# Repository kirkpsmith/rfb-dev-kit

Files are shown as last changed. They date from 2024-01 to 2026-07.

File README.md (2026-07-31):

# RFB-dev-kit



[Certified](https://certification.oshwa.org/fr000028.html) by OSHWA

--------------------------------------------------------------------------------
## About

This kit is for testing flow battery components and electrolytes at a benchtop scale (2 cm²) with an affordable, reproducible setup.

Developed by the [Flow Battery Research Collective](https://fbrc.dev).

Assembled cell

View of electronics in jig

## Documentation

Documentation to build the kit, which includes the BOM, is available [here (latest version, with file previews)](https://fbrc.codeberg.page/rfb-dev-kit/), or locally in the repo [here (current version, without file previews)](docs/_site/index.html).

## Design Choices

- Maximize off-the-shelf component and material availability.
- Impervious graphite or polymer-graphite composite materials are hard to source. Instead we use graphite foil, which is affordable, easily sourceable and works well enough to perform cycling experiments at this scale.
- No flow fields. We use flow-through graphite felt porous electrodes, and the design is parametric to handle different thicknesses
- No milling of graphite or plastic.

## Repository Structure

- `CAD` directory: FreeCAD and KiCAD design files
    - `FreeCAD` directory: FreeCAD files
    - `KiCAD` directory: KiCAD project files
    - `exports` directory: files for manufacturing components and rendering documentation
    - `imports` directory: files imported by FreeCAD for creating assembly
- `docs` directory: documentation written with [GitBuilding](https://gitbuilding.io/)
- `firmware` directory: code for pump speed controllers based on Arduino Uno R3

## Contributing

Please see the [contributing guide](https://fbrc.dev/contributing.html) on our website!

## Community

Discussion about the project happens on the [FBRC forum](https://fbrc.nodebb.com/)!

## References/Inspiration/Collaborators/Conspirators (in no particular order)
- [FAIR Battery project](https://github.com/SanliFaez/FAIR-Battery) (collaborators)
- White, R. E. Electrochemical Cell Design; Springer US: Boston, MA, 1984.
- O’Connor, H.; Bailey, J. J.; Istrate, O. M.; Klusener, P. A. A.; Watson, R.; Glover, S.; Iacoviello, F.; Brett, D. J. L.; Shearing, P. R.; Nockemann, P. An Open-Source Platform for 3D-Printed Redox Flow Battery Test Cells. Sustainable Energy Fuels 2022, 6 (6), 1529–1540. https://doi.org/10.1039/D1SE01851E.
- Arenas, L. F.; Walsh, F. C.; León, C. P. de. 3D-Printing of Redox Flow Batteries for Energy Storage: A Rapid Prototype Laboratory Cell. ECS J. Solid State Sci. Technol. 2015, 4 (4), P3080. https://doi.org/10.1149/2.0141504jss.
- https://codeberg.org/LibreWater/Acraea-Prototype
- https://github.com/opulo-inc/lumenpnp/tree/main
- https://openflexure.org/

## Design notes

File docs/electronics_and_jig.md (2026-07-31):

---
Details:
    Time: Tens of minutes
    Skills:
      - Soldering
      - Flashing firmware to an Arduino 

---
<!-- There should be only one Header per page. You do not need to use all the keys -->
# Preparing the jig with pumps and power electronics

{{BOM}}

## System overview

A [computer]{cat:tool, qty:1, Note:Must be able to flash firmware to microcontroller and connect over USB serial to microcontroller and potentiostat} communicates with both a charging/discharging device (typically a [potentiostat](pstat.md){cat:tool, qty:1, note: preferably the MYSTAT}) as well as an [Arduino UNO R3]{qty:1, Note:or equivalent microcontroller that can output two independent 5V PWM signals and connect to the computer over USB serial}. These documents assume the use of a MYSTAT potentiostat and it's [modified control software](https://codeberg.org/FBRC/mystat/).

The Arduino is connected to two peristaltic pumps which have internal stepper motor drivers, and are powered by a [24 V DC power source]{cat: part, qty: 1}. To know the flowrate (in mL/min) of the peristaltic pumps, a separate measurement is required (like dispensing water into a graduated cylinder).

We use the open-source MYSTAT (with our own modifications to the control software), but any equivalent potentiostat or battery cycler will do. Our pump control system is based on the MYSTAT software, though, and can be used without the MYSTAT present.

With this hardware configuration, the MYSTAT software then allows for entire control of this electrochemical system: the applied currents and voltages as well as the speeds of the electrolyte pumps. 

## Flash firmware to microcontroller {pagestep}

Using the Arduino IDE with the elapsedMillis library installed, upload the following code to the Arduino. The location of the code in the repository is [here](https://codeberg.org/FBRC/RFB-dev-kit/src/branch/main/firmware/ArduinoUnoR3_MotorControl.ino)

## Solder the wiring harness

Using a [soldering iron]{cat: tool, qty: 1}, take the [peristaltic pumps with correct tubing](fromstep){qty: 2}, [DC power jack]{cat: part, qty: 1} and solder them to the Arduino according to the following schematic:


>! **Caution** 
>!
>! Be sure to connect the Arduino ground to the power supply ground of the pumps so that the PWM and tachometer signals work properly

## Assemble the pump controller case

Taking the soldered Arduino, pumps, and DC power jack, assemble them into the [pump controller case parts](fromstep){qty: 1} as shown:



The pump wiring is fed through the long narrow slots in the pump controller case base so that it can be assembled into the case post-soldering.

## Add pumps and controller case to jig {pagestep}

Insert the pumps into their holders in jig while aligning the pump controller case mounting holes with their matching holes on the jig. Fasten with eight [M3x35mm socket cap bolts and nuts]{qty: 8,cat: part}.



>i **Note** 
>i
>i The reset button is placed with the large end *inside* the case

##Connect microcontroller to PC and test pumps{pagestep}

We are using the MYSTAT potentiostat and have modified the software to be able to control the pump speeds. If you have a different potentiostat, you can still use the MYSTAT software to control your pumps without having a MYSTAT connected.

Plug in the 24V power supply cable to the jack on the case.. Connect the Arduino to the PC with a [USB A-to-B cable]{qty: 1,cat: part}.

Run the MYSTAT [modified control software](https://codeberg.org/FBRC/mystat/releases).

Connect to the Arduino through the MYSTAT GUI. Briefly test each pump to make sure it spins (it can spin for a couple seconds dry without issues).



## Add tubing and connectors to top pump connections {pagestep}

Add two pieces of [4 cm cut tubing](fromstep){qty: 2} to the upper barbed fittings of each pump. Add a [F-31 Luer Lock Adapter][F-31 Luer Lock Adapters]{cat: part, qty: 2} to the other end of each piece of tubing.

>i **Note** 
>i
>i The tubing here is shown bent according to it's final shape after cell assembly, this will happen naturally when the cell is installed.



## Add reservoirs to jig {pagestep}

Insert the [combined reservoir with tubing](fromstep){qty: 1} into the jig as shown, connecting the shorter tubing on the inner barbs of the reservoirs to the bottom connection of the pump. The reservoirs should "click" into place into the holding mechanism on the jig.
The flexible tubing will eventually take on a shape similar to what is shown when the cell is installed.



[assembled jig]{output, qty: 1}

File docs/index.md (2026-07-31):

# Building a benchtop flow battery test cell

>i **Note** 
>i
>i This kit is intended for educational and R&D use only, not for actual energy storage applications. That will happen later, check out our [roadmap](https://fbrc.dev/about.html#roadmap) to see when.
>i
>i Project homepage is at https://fbrc.dev, source code for this documentation is [here](https://codeberg.org/FBRC/RFB-dev-kit).





This bill of materials can be found [here]{BOM}.

If you're starting from scratch, you need to [fabricate](fabrication.md) and source everything needed for using this flow battery test cell.

If you already have all the required components and materials, you can directly [prepare the electronics and jig](electronics_and_jig.md), [assemble the cell](cell_assembly.md), [install the cell into the jig](final_jig_assembly.md], prepare the [electrolyte](electrolyte.md), [leak test](leak_test.md) and then begin [testing](testing.md). After an experiment, you should [clean up](cleanup.md) your setup and [analyze](analysis.md) the data you obtained.

1. [.](fabrication.md){step}

2.  [.](electronics_and_jig.md){step}

3. [.](cell_assembly.md){step}

4. [.](final_jig_assembly.md){step}

5. [.](leak_test.md){step}

6. [.](electrolyte.md){step}

7. [.](testing.md){step}

8. [.](cleanup.md){step}

9. [.](analysis.md){step}

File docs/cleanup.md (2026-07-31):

---
Details:
    Time: Tens of minutes
    Skills:
      - General chemistry laboratory skills 
---
<!-- There should be only one Header per page. You do not need to use all the keys -->
# Stopping and disassembling the cell

Once your experiment has concluded, save your data files, power down and disconnect the potentiostat.

Stop the pumps and drain the electrolyte from the reservoirs into a waste container. Add water and run the pumps for several seconds to rinse the cell and tubing. Repeat until the drained solution is clear.

Handle chemical waste according to local regulations.

Disconnect the cell from the jig in four locations, leaving the tubing attached to all four barbs/ports of the two flow frames:

- at each pump, going from the pump to the flow frame (x2)
- at the double-ended barbed fittings between the flow frame and the reservoir inlet (x2)



Take apart the cell, noting that you can leave the tubing attached to the flow frames.

Make any observations you might have of the separator (note which way it was facing when you do so), positive and negative electrodes, *etc.*

Clean and store the reusable cell components.

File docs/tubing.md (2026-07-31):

---
PartData:
    Specs:
        Brand: Masterflex
        Type: Chem-Durance Bio Tubing
        Inner Diameter: 3.2 mm
        Outer Diameter: 6.4 mm
    Suppliers:
        Drifton (EU):
            PartNo: 06442-16
            Link: 'https://www.drifton.eu/shop/18-standard-pump-tubing/2535-chem-durance-bio-tubing-15-m/'
        Avantor (US):
            PartNo: 06442-16
            Link: 'https://www.avantorsciences.com/us/en/product/NA5143626/masterflex-ls-precision-pump-tubing-chem-durance-bio-avantor'
---

# Tubing

This tubing is made from a BPT-like exterior tubing with a PTFE-like liner which is good for flow battery chemical compatibility. It used to be called "Tygon Chemical" tubing and still is in some places.

>!! **Warning** 
>!!
>!! PTFE-lined tubing in the pump head is essential for electrolytes which contain iodide, as charged iodide species can destroy common pump head tubing materials like silicone and BPT



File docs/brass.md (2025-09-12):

---
PartData:
    Specs:
        Thickness: 1.0 mm
    Suppliers:
        Amazon:
           PartNo: Use this link
           Link: 'https://www.amazon.com/dp/B0BRCXM73P'

---

## Brass current collectors



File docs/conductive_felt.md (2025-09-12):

---
PartData:
    Specs:
        Material: Conductive Graphite Felt
        Thickness:  3.2 mm or 1/8 inch
    Suppliers:
        Fisher Scientific:
            PartNo: AA43199RY 
            Link: 'https://www.fishersci.com/shop/products/carbon-felt-3-18mm-0-125in-thick-99-0-thermo-scientific/AA43199RY#?keyword=043199'
        AliExpress:
            PartNo: Link
            Link: 'https://www.aliexpress.com/item/1005008240523112.html'

---

# Conductive Graphite (Carbon) Felt
The Fisher Scientifics carbon felt is commonly used in academic studies. There are other more affordable suppliers on AliExpress and specialty carbon product suppliers in various regions worldwide. The felt needs to be conductive, this technically means it has to have been "graphitized" and thermally treated at a sufficiently high temperature, though sometimes it may still be sold as "carbon felt" as in the Fisher Scientific product.

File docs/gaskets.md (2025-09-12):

---
PartData:
    Specs:
        Material: Silicone
        Thickness: 0.1 mm
    Suppliers:
        Amazon (FR):
            PartNo: Link
            Link: 'https://www.amazon.fr/dp/B09HZ52B8H'
        AliExpress:
            PartNo: Link
            Link: 'https://www.aliexpress.com/item/1005007892725572.html'

---

# Gasket material

This is used to cut gaskets.



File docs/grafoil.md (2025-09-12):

---
PartData:
   Specs:
      Thickness: 0.5 mm
   Suppliers:
      RS Components:
         PartNo: 268-6953 (1.0 mm, slightly thicker)
         Link: https://uk.rs-online.com/web/p/gasket-sheets/2686953
      Amazon (NL):
         PartNo: Use this link
         Link: 'https://www.amazon.nl/-/en/NEZIH-flexible-graphite-sheet-conductive/dp/B0CF88BKNX'
      Amazon (US):
         PartNo: Use this link
         Link: 'https://www.amazon.com/dp/B09MSDYKNF'
---

## Grafoil sheet

Grafoil sheet is compressed graphite commonly used in industry as high-temperature gasket material. It is affordable and similar enough for our purpose here to bipolar plate material, which is much harder to source.

Note that you cannot find this on AliExpress anymore due to export restrictions or similar.



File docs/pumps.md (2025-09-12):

---
PartData:
    Specs:
        Brand: Kamoer
        Model: KPK200
        Motor: Brushless
        Voltage: 24 V
    Suppliers:
        Alibaba:
            PartNo: Use this link
            Link: 'https://www.alibaba.com/product-detail/Kamoer-KPK200-12V-24V-Brush-Brushless_1601189956284.html'
        AliExpress:
            PartNo: Use this link
            Link: 'https://www.aliexpress.com/item/1005009259643053.html'
---

# Peristaltic pumps



After trying many peristaltic pumps this one seems to work well when paired with the right tubing.

Here is the datasheet for these pumps:


>! **Caution** 
>!
>! Make sure to get the KPK200 24B motors. Send the merchant a message after you make the purchase to specify the pump. Make sure to be clear about needing the specific pump model because you have a project with dimensions for that specific pump. They have sent more expensive pumps in the past because these were just not in stock. Tell them it HAS to be KPK200 24B.

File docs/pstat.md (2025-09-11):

---
PartData:

    Suppliers:
        PCBWay:
            PartNo: Use this link
            Link: 'https://www.pcbway.com/project/shareproject/MyStat_Potentiostat_9df57df2.html'
---

# Potentiostat

The MYSTAT potentiostat allows you to control the voltage or current through the cell and record and plot both parameters. You can order the PCB including components through the PCBWay project linked below.

>i **Note**
>i
>i You can also use another battery cycler or galvanostat/potentiostat with appropriate specifications, but this documentation uses the MYSTAT.

>!! **Warning** 
>!!
>!! The potentiostat has two analog-digital converters. There are three options of components to choose from,one for 50Hz grids like in Europe, one for 60Hz grids like in US America and one that can do both. Be sure to upload a BOM with the correct version for your grid. The 50Hz version of the ADC is called MCP3550-50, the 60Hz one is called MCP3550-60 and the universal one is called MCP3553.

In order to get the potentiostat working, you first need to program it's PIC16 microcontroller using a special PIC programmer like the PICkit and the programming software by Microchip. The version needed for the voltage-range extended MYSTAT can be found [here](https://codeberg.org/FBRC/mystat/src/branch/master/firmware/firmware.hex).

The python-based control software can be found [here](https://codeberg.org/FBRC/mystat/src/branch/master/python), it serves both as a potentiostat and galvanostat control and visualization software but can also control the pumps.

>i **Note**
>i
>i You need to fabricate a cable that connects the potentiostat to the cell, based on a 2.5 mm audio jack cable with 4 leads exposed.

>!! **Warning**
>!! 
>!! Never connect or disconnect the jack-cable while the power is still connected as the jack connects to random leads during insertion or removal from the socket.

>i **Note**
>i
>i Be sure to connect the potentiostat to the power supply before you do the calibration or use it for measurement.

Once you can successfully connect to the potentiostat, you need to calibate it, this procedure is explained in the [MYSTAT paper](https://doi.org/10.1016/j.ohx.2020.e00163) and the [paper](https://doi.org/10.1016/j.ohx.2017.08.001) describing the predecessor of MYSTAT.

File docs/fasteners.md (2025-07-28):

---
PartData:
    Specs:
        Material: Titanium (for testing iodide-containing electrolyte), otherwise stainless steel
        Length: 35 mm
        Size: M6
        Head: Hex Socket Cap
---

# M6 Fasteners

Four M6 x 35 mm hex socket cap nuts and bolts (with washers) are used to compress the cell.

For iodide-containing electrolytes, trace triiodide remaining in the cell during disassembly can deteriorate stainless steel, zinc-coated, and mild steel fasteners, which is why titanium is recommended for routine usage.

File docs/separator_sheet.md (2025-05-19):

---
PartData:
    Specs:
        Material: Matte Photo Paper
        Weight:  230 g/m²
    Suppliers:
        Amazon:
            PartNo: Use this link
            Link: 'https://www.amazon.fr/gp/product/B07JYT7BN8/'
---

# Separator material



This is good enough separator material to get started, though a real battery separator like Daramic is preferred (but hard to obtain).

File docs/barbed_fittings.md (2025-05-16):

---
PartData:
    Specs:
        Barb: For 3.2 mm (1/8") ID flexible tubing
    Suppliers:
         AliExpress:
            PartNo: Use this link
            Link: ''
         Amazon:
            PartNo: Use this link
            Link: ''

---

## Barbed fittings

Also try searching for "Pagoda fittings" for other suppliers

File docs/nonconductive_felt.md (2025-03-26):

---
PartData:
    Specs:
        Material: Polypropylene
    Suppliers:
        Amazon:
            PartNo:  AA43199RY 
            Link: 'https://www.fishersci.com/shop/products/carbon-felt-3-18mm-0-125in-thick-99-0-thermo-scientific/AA43199RY#?
keyword=043199'

---

# Nonconductive Felt

This can be used as a spacer on the negative side, to allow metal to plate. It also can be used as a spacer on the cathode side, to prevent clogging of the cell in the event of solid iodine precipitation.

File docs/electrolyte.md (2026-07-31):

---
Details:
    Time: Tens of minutes
    Skills:
      - General chemistry laboratory skills
---
# Preparing the electrolyte

>! **Caution** 
>!
>! From this point onwards, chemical safety risks are present. **You** are responsible for your own safety! Use proper PPE and do not perform anything you are not comfortable with. These instructions are presented as-is with no guarantee of your safety or assumed liability. Work in a well-ventilated area, with someone else nearby aware that you are working with chemicals and able to assist or call for help if needed.

There are many possible electrolytes that can be tested with this test cell depending on the membrane and reservoir configuration shown. This documentation is chemistry-agnostic; you are free to choose your own chemistry depending on what you'd like to study. Typically, the cell is loaded with 5 mL of electrolyte per side. [prepared electrolyte]{output, qty: 10 mL, hidden}.

For an example of some electrolytes that have been testing, check out the FBRC forum category for [electrolyte development](https://fbrc.nodebb.com/category/6/electrolyte-development).

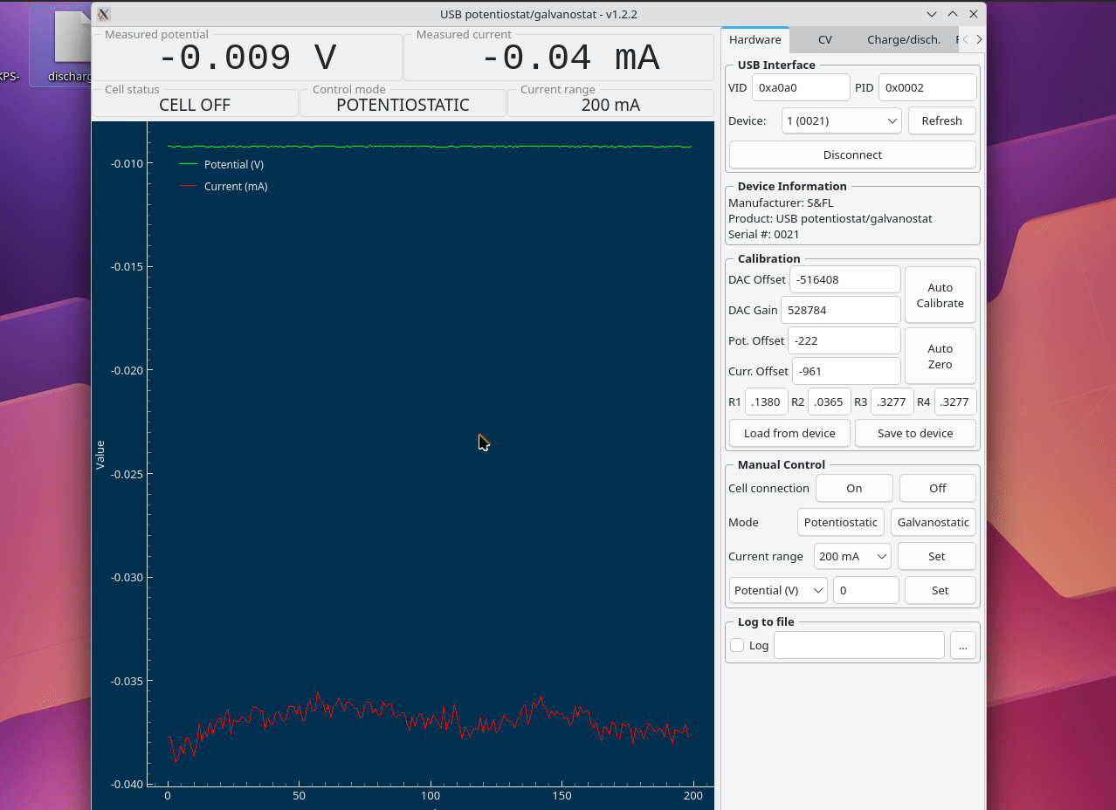
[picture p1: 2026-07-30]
docs/images/Peek2026-07-2921-43.gif

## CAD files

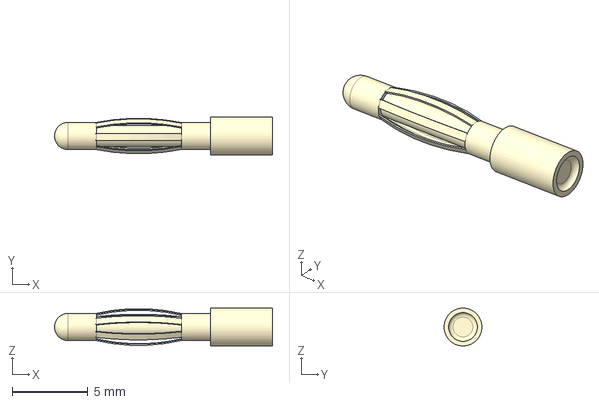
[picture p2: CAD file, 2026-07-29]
CAD/imports/Pin_PCB-Male.step
14.4 x 2.50 x 2.50 mm

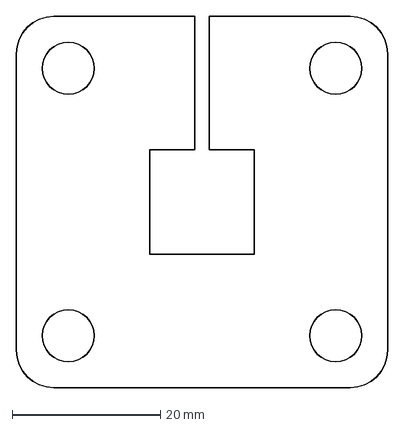
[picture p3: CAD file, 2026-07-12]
CAD/exports/static-frame-2D-Page.dxf
50.0 x 50.0 mm

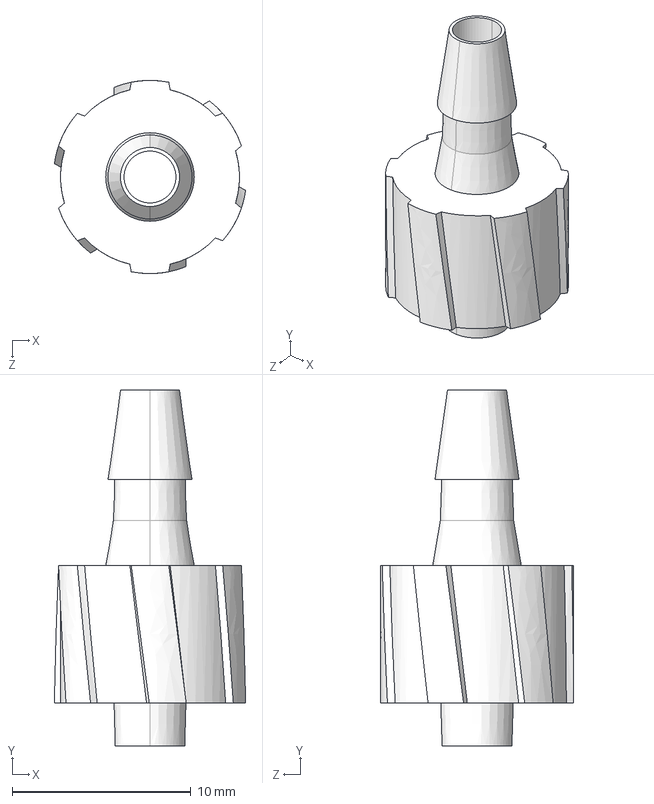
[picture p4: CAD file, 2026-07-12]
CAD/imports/male luer lock 37.STEP
10.7 x 19.9 x 10.8 mm

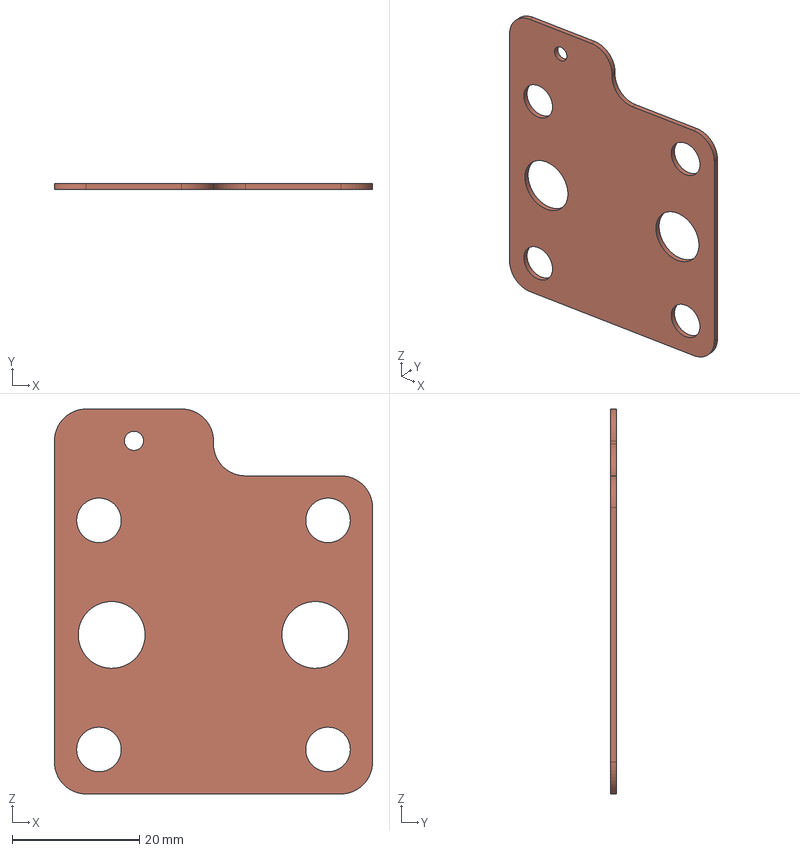
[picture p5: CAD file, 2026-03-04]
CAD/exports/Current Collector.step
50.0 x 1.00 x 60.5 mm

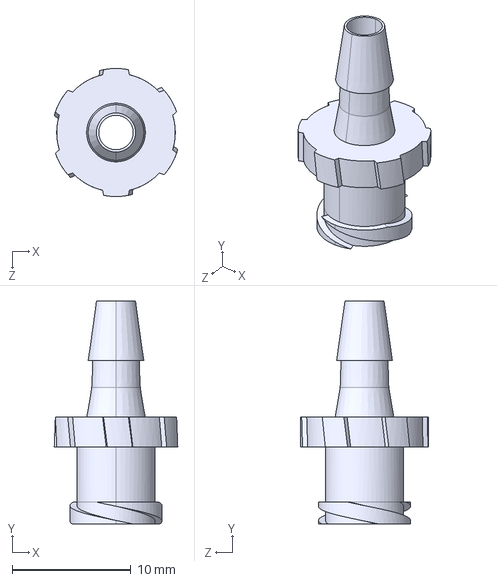
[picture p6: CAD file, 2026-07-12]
CAD/imports/female luer lock 37.STEP
10.4 x 18.8 x 10.8 mm

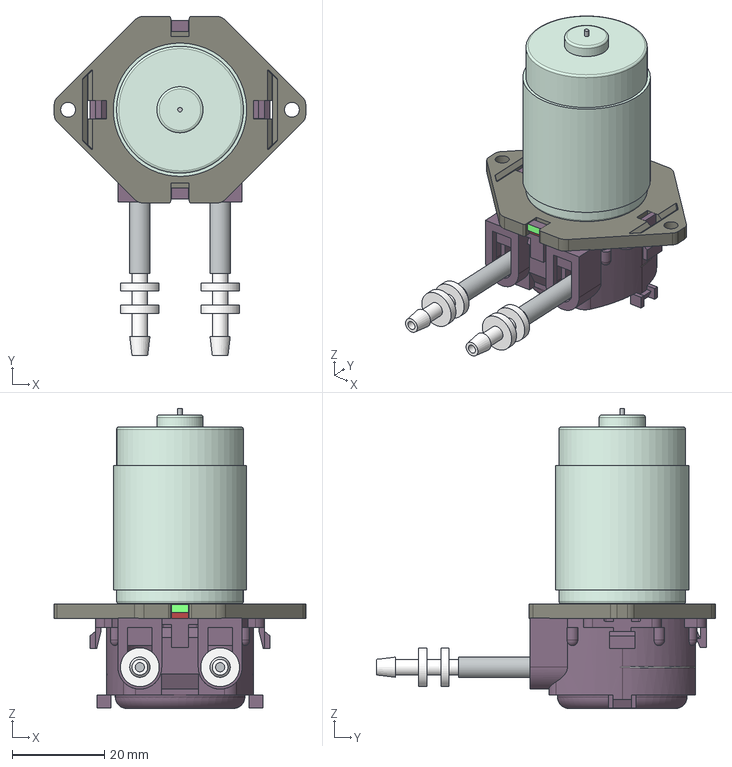
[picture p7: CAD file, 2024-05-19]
CAD/imports/peristaltic pump KPP from kamoer.stp
54.5 x 73.6 x 65.0 mm
ﾈ荼ｯｱﾃ ｿｨﾄｬｶ瑢amoer KPP 0070C18C45
软管接头 kamoer蠕动泵接头 宝塔形 3.4-3.4 适 x 2

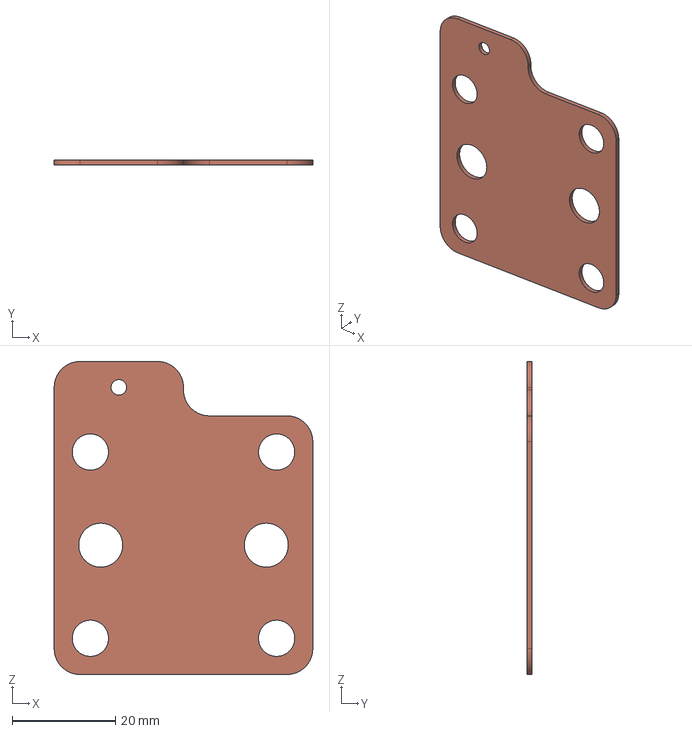
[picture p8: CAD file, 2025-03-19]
CAD/exports/outer-current-collector-Cu Plate.step
50.0 x 1.00 x 60.5 mm

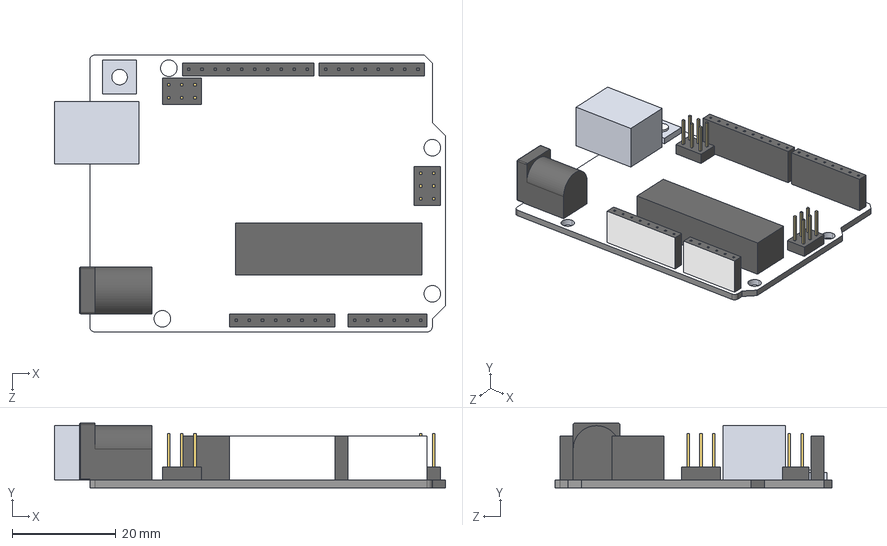
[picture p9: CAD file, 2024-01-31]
CAD/imports/arduinoUnoSimplified.STEP
75.4 x 12.5 x 53.4 mm

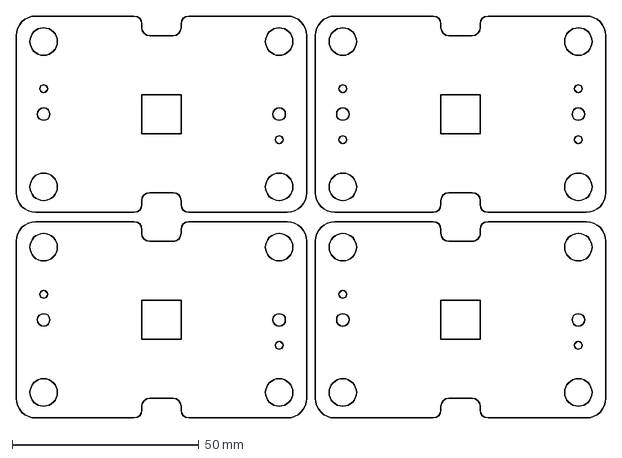
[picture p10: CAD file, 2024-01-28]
CAD/exports/all_gaskets.dxf
157.7 x 107.5 mm

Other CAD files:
CAD/FreeCAD/assembly.FCStd
CAD/FreeCAD/cell-assembly.FCStd
CAD/FreeCAD/cell-assembly-tool.FCStd
CAD/exports/Double-Reservoir-without-Spillover.stl
CAD/FreeCAD/19-22-septa.FCStd
CAD/exports/reset_button.stl
CAD/FreeCAD/Params.FCStd
CAD/FreeCAD/double-reservoir.FCStd
CAD/FreeCAD/jig.FCStd
CAD/FreeCAD/CFD.FCStd
CAD/FreeCAD/Clamp.FCStd
CAD/FreeCAD/GN_Container.FCStd
CAD/FreeCAD/endplate-hole.FCStd
CAD/FreeCAD/endplate-pin.FCStd
CAD/FreeCAD/flow-frame.FCStd
CAD/FreeCAD/inner-current-collector-CAM.FCStd
CAD/FreeCAD/inner-current-collector.FCStd
CAD/FreeCAD/inner-gasket.FCStd
CAD/FreeCAD/luer-tool.FCStd
CAD/FreeCAD/membrane-frame.FCStd
CAD/FreeCAD/membrane.FCStd
CAD/FreeCAD/outer-current-collector.FCStd
CAD/FreeCAD/outer-gasket.FCStd
CAD/FreeCAD/porous-electrode.FCStd
CAD/FreeCAD/reservoir.FCStd
CAD/FreeCAD/static-frame-2D.FCStd
CAD/FreeCAD/static-frame-acrylic.FCStd
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

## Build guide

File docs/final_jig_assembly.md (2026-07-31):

---
Details:
    Time: Tens of minutes
    Skills:
      - Mechanical assembly
---
<!-- There should be only one Header per page. You do not need to use all the keys -->
# Attaching the assembled cell to the jig
Gather the following components:
{{BOM}}

## Rotate the assembled cell away from the jig and connect lower tubing connections {pagestep}

Take the [assembled flow cell](fromstep){qty:1} and place it into the [assembled jig](fromstep){qty: 1}. Rotate the cell so the clamp is facing up; this makes it easier to connect the lower tubing connections first. Connect the lower tubing of the cell to the 9 cm tubing length pieces coming from the reservoir outlets as shown, twisting together the Luer Lock fittings tightly to seal.





## Rotate the cell towards the jig and connect upper tubing connections {pagestep}

Now that the lower tubing Luer fittings are connected, rotate the cell upwards and connect the remaining fittings as shown.





>!! **Warning** 
>!!
>!! Avoid creating kinks and sharp bends in the tubing when assembling the cell. This can create issues with electrolyte flow.

>!! **Warning** 
>!!
>!! Electrolyte flow must flow from bottom of the cell upwards to top, in order to clear out gas bubbles from the cell and ensure good liquid electrolyte flow

## Place the jig into secondary containment {pagestep}

Place the entire assembled jig into a [secondary container]{cat: part, qty: 1, Note: "Gastronorm 1:3 150mm deep polypropylene works well"}

The kit has been designed to fit into a GN 1:3 150 mm deep plastic container.



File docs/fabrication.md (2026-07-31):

---
Details:
    Time: Hours
    Skills:
      - 3D printing or milling
      - Drilling
      - Cutting

---
<!-- There should be only one Header per page. You do not need to use all the keys -->
# Fabricating components

## Bill of Materials

{{BOM}}

You will need a [FDM printer]{qty:1, cat:tool} and at least two types of filament, [stiff filament]{qty: some, Note: PLA works} and [polypropylene filament]{qty: some, Note: This can be substituted if you only plan to run water through the cell for testing things other than the chemistry}.

## Print one jig and one cell assembly tool{pagestep}

Print the [jig]{output, qty: 1} and [cell assembly tool]{output, qty: 1} in PLA or whatever material you can print easily. It does not have to be chemically resistant or that strong, so you can use a low infill.





## Print Arduino Uno case parts{pagestep}

These parts can be done in PLA or similar filaments at low infill. They mount onto the back of the jig.





[pump controller case parts]{output, qty: 1, hidden}

>i **Note** 
>i
>i [3D Printed Case for Arduino Uno, Leonardo](https://github.com/zygmuntw/3D-Printed-Case-for-Arduino) by ZygmuntW is licensed under the Creative Commons - Attribution - Share Alike license.

## Print two endplates{pagestep}

Print one of each endplate: [endplate with holes]{output, qty: 1} and [endplate with pins]{output, qty: 1}. They must be stiff, so print them with at least 70% infill in PLA or PETG. Try to avoid warping as they bottom need to be flat to seal the cell well.





## Print wetted cell components in polypropylene{pagestep}
 
Print the combined reservoir and two flow frames **in polypropylene**.

It's important these don't leak. Leak-tight parts in FDM require trial-and-error, we have found good conditions for printing to be at 100% infill, 7 perimeters/wall lines, 1.05 flowrate multiplier (5% overextrusion), and a line width of 0.45 mm (for a 0.4 mm nozzle).

>? **Help Block** 
>?
>? It's important these don't leak. Leak-tight parts in FDM require trial-and-error, we have found good conditions for printing to be at 100% infill, 7 perimeters/wall lines, 1.05 flowrate multiplier (5% overextrusion), and a line width of 0.45 mm (for a 0.4 mm nozzle).





>!! **Warning** 
>!!
>!! The total combined thickess of the flow frames and (compressed) gaskets is important! The compression is fixed by the combined total thickness of the flow frame and two gaskets.

## Cut gaskets {pagestep}

>i **Note:**
>i
>i Cutting the gaskets is most easily done with a vinyl cutter machine or laser cutter, but can also be done manually with a steady hand, utility blade, and appropriately sized punches.

Using a [gasket cutter machine]{qty: 1, cat:tool, Note: Vinyl/laser cutter or hand tools}, download the gasket file and cut a sheet of [gasket material][gasket sheet](gaskets.md){qty: 160 cm², note: "Dimensions must be at least enough to cut out approx. four 6 cm x 8 cm rectangles, an A4 sheet is enough" } to make the following four gaskets:





[inner gaskets]{output, qty: 2, hidden} [outer gaskets]{output, qty: 2, hidden}

## Cut porous electrodes {pagestep}

Cut two conductive graphite felt electrodes to fit inside the flow frames using scissors or a [utility knife]{qty: 1, cat:tool}. Our current standard test uses 2 cm² geometric area cells, so cut two squares each with a side length of 14.1 mm from a larger piece of [conductive felt](conductive_felt.md){qty: 4 cm², cat: part}.

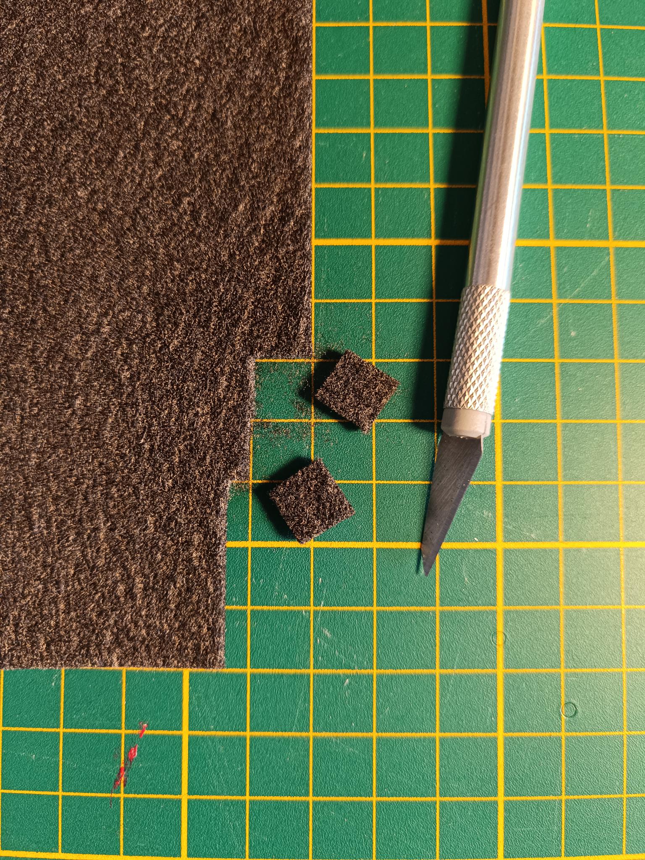
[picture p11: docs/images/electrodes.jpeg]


[cut electrodes]{output, qty: 2, hidden}

## Cut separator membrane {pagestep}

Cut [separator sheet](separator_sheet.md){qty: A4 sheet,cat: part} into a 2.7 cm x 2.7 cm square (depending on your material, you may need multiple layers to stack to sufficient thickness).

[cut membrane]{output, qty: 1, hidden}

## Cut grafoil current collectors {pagestep}

Using a precut gasket as a guide, cut/punch [grafoil](grafoil.md){qty: 100 cm²} into the following shape to make [grafoil current collectors]{output, qty: 2}. An appropriate gasket cutter machine can also be used but note that a CO₂ laser cannot cut graphite.



## Cut brass current collectors {pagestep}

Using a [2D metal cutting tool]{qty: 1, cat:tool,Note: "Mill, drill, router, laser cutter for sheet metal"}, machine [1 mm brass sheet](brass.md){qty: a small plate of} according to the below drawing to make two [brass current collectors]{output, qty: 2}. Alternatively [the .step file](../CAD/exports/Current-Collector.step) can be used with 2D fabrication services to order the cut parts.



## Ensure correct tubing type is in peristaltic pumps {pagestep}

If you plan to test zinc-iodide chemistries, you need PTFE-lined peristaltic pump tubing loaded in your [peristaltic pumps](pumps.md){qty: 2} [peristaltic pumps with correct tubing]{output, qty:2, hidden}

>!! **Warning** 
>!!
>!! Your pump may not come with PTFE-lined tubing installed, you should verify what type is installed before running your first experiment

## Cut tubing {pagestep}

Cut [tubing](tubing.md){qty: 54 cm} into the following lengths:

- 4x 3.5 cm pieces (flow frame connections to Luer Lock fittings)
- 2x 4 cm (pump to flow frame Luer Lock fitting)
- 2x 7 cm pieces (pump outlet to reservoir inlet)
- 2x 9 cm pieces (reservoir outlet to flow frame Luer Lock fitting)

[4 cm cut tubing]{output, qty: 2, hidden}

>? **Help Block** 
>?
>? The tubing-printed barb connections are difficult to attach, the fit is very tight. Softening the ends of the tubing in hot water before pushing them on can help immensely.

## Attach tubing to the barbed fittings {pagestep}

Take the two flow frames and attach one piece of 3.5 cm tubing to each barb. It should be a tight fit. You will only have to do this once.

Then, insert [F-25 Luer Lock Adapters]{cat: part, qty: 4} Into the ends of the tubing.



[flow frames with tubing and adapters]{output, qty: 2, hidden}

## Attach tubing and two adapters to the reservoirs {pagestep}

Insert two [F-31 Luer Lock Adapters]{cat: part, qty: 2} into the ends of the 9 cm tubing.



[combined reservoir with tubing]{output, qty: 1, hidden}

## Attach banana connectors to the outer current collectors {pagestep}



Take two [2 mm banana connectors with M2 thread and matching nuts]{cat: part, qty: 2} and fasten them to the outer current collectors as shown above.

>!! **Warning** 
>!!
>!! Be sure to make mirrored left- and right-handed versions of the current collectors with the connectors installed. In the assembled cells, the tabs must be opposite each other but the elecrical connections are done from the same side.

[outer current collectors with banana connector]{output, qty: 2, hidden}

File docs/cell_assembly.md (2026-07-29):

---
Details:
    Time: Tens of minutes
    Skills:
      - Mechanical assembly
---
<!-- There should be only one Header per page. You do not need to use all the keys -->
# Assembling the flow cell from components

Ensure you have the following components:
{{BOM}}

Refer to the following diagram for the cell assembly process.



## Place the endplate on the cell assembly tool {pagestep}

Take the [cell assembly tool](fromstep){qty: 1} and place the [endplate with pins](fromstep){qty: 1} with the pins pointing upwards.

## Add the brass current collector {pagestep}

Make sure the large tubing holes of the [outer current collector with banana connector][outer current collectors with banana connector](fromstep){qty: 1} align with the endplate.

## Add the negative grafoil current collector {pagestep}

Make sure the large tubing holes of the [grafoil current collector][grafoil current collectors](fromstep){qty: 1} align with the brass current collector.

## Add the negative outer gasket {pagestep}

Place one [outer gasket][outer gaskets](fromstep){qty: 1} on top of the assembly, using the bolts to guide the gasket and align it with the fluid holes in the cell body.

## Add the negative flow frame {pagestep}

Place one [flow frame with tubing and adapters][flow frames with tubing and adapters](fromstep){qty: 1} on top of the assembly, with the barbs and tubing facing downward into the cell assembly tool.

>? **Help Block** 
>?
>? The total combined thickess of the flow frames and (compressed) gaskets is key to achieving the desired results! The graphite felt should be compressed to 70% of it's original thickness. The compression is fixed by the combined total thickness of the flow frame and two gaskets.

## Add the negative graphite felt{pagestep}

Place one [graphite felt][cut electrodes](fromstep){qty:1} on top of the assembly.

## Add the negative inner gasket{pagestep}

Take one [inner gasket][inner gaskets](fromstep){qty: 1} and add it to the assembly.

## Add the membranes {pagestep}

Take the [cut membrane](fromstep){qty: 1} and add it to the assembly (you may be using multiple layers of a single material here depending on your experiment).

## Add the positive inner gasket{pagestep}

Take one [inner gasket][inner gaskets](fromstep){qty: 1} and add it to the assembly.

## Add the positive flow frame {pagestep}

Place one  [flow frame with tubing and adapters][flow frames with tubing and adapters](fromstep){qty: 1} on top of the assembly.

## Add positive outer gasket {pagestep}

Place one [outer gasket][outer gaskets](fromstep){qty:1} on top of the assembly.

## Add positive graphite felt{pagestep}

Place one [graphite felt][cut electrodes](fromstep){qty:1} on top of the assembly.

## Add the positive grafoil current collector {pagestep}

Place the positive [grafoil current collector][grafoil current collectors](fromstep){qty: 1} over the flow frame.

## Add the positive brass current collector {pagestep}

Place the positive [outer current collector with banana connector][outer current collectors with banana connector](fromstep){qty: 1} on the cell as shown so the tab is facing opposite the negative current collector tab, but on the same side of the cell.

## Add the positive endplate {pagestep}

Place the [endplate with holes](fromstep){qty: 1} on top of the assembly.

## Tighten with C-clamp {pagestep}

Remove the cell carefully from the Cell Assembly Tool. It should now look like this:



Now, take a [50 mm C-clamp]{cat: part, qty: 1, Note: "Also known as G-clamp, 2-inch varieties should work"}, place it on the cell as shown below, and tighten it to seal the cell.



**Now you have an [assembled flow cell]{output, qty:1}!**

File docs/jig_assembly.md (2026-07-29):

---
Details:
    Time: Tens of minutes
    Skills:
      - Mechanical assembly
---
<!-- There should be only one Header per page. You do not need to use all the keys -->
# Assembling the jig with electronics and flow cell

Gather the following components:
{{BOM}}

## Add reservoirs to jig {pagestep}

Insert the [combined reservoir with tubing](fromstep){qty: 1} into the [jig with pumps and power electronics](fromstep){qty: 1} as shown:

## Add cell to jig and connect to tubing {pagestep}

Take the [assembled flow cell](fromstep){qty:1} and place it into the jig, connecting the tubing as described and shown:

Take the rest of the tubing and connect the lengths as so, for both positive and negative half-cells:
- pump outlet to inlet of cell (on bottom)
- outlet of cell (on top) to long barb on reservoir
- short barb on reservoir to pump inlet

Same tubing principles apply for peristaltic pumps

>!! **Warning** 
>!!
>!! Avoid creating kinks and sharp bends in the tubing when assembling the cell. This can create issues with electrolyte flow.

>!! **Warning** 
>!!
>!! Electrolyte flow must flow from bottom of the cell upwards to top, in order to clear out gas bubbles from the cell and ensure good liquid electrolyte flow

This makes an [assembled test jig]{output, qty: 1}.

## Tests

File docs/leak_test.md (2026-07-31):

---
Details:
    Time: Tens of minutes
    Skills:
      - Mechanical assembly
      - Visual inspection
---
<!-- There should be only one Header per page. You do not need to use all the keys -->
# Leak testing the cell
{{BOM}}

## Connect the motor control electronics to PC {pagestep}

Place the system on a surface that can get wet in case of possible leakage.

Making sure the motor control electronics are powered, plug the USB cable of the Arduino into the [PC]{qty: 1, cat: Tool} and connect to the Arduino using the MYSTAT software.

>!! **Warning** 
>!!
>!! Don't get your computer wet!

## Add water to reservoirs {pagestep}

Add about 5 mL of [deionized water]{qty: 10 grams, cat: chemical} to each reservoir.

## Turn on the pumps {pagestep}

From the MYSTAT software, turn on both pumps at 40% speed.

## Inspect cell and reservoirs for leakage {pagestep}

>? **There are two types of leakage** 
>?
>?  **External leakage**, which is obvious: water coming from the gaskets, reservoir, a faulty connection, *etc.* The other is **internal leakage**, when the membrane is not properly sealed, has a hole, or similar, which creates flow between the two half-cells that shouldn't exist. This shows up as a rapid imbalance of volume between the two reservoirs.

Run the pumps for at least two minutes and monitor the internal levels of both reservoirs. They should not change appreciably. If the cell does not show signs of external or internal leakage, great!

## Empty reservoirs {pagestep}

Grab two [50 mL beakers]{qty:2, cat: tool, Note: or drip tray/other container to hold 10 mL of water} and space them out so that you can invert the entire jig (with pumps running) and pour out the water from the reservoirs into the beakers. Let the pumps run a few seconds to squeeze the water from the tubing lines and cell body.

>? **Why is this important?** 
>?
>? Getting rid of the as much water as possible is important for reproducibility so that we test electrolytes as close to the intended concentration as possible. If extra water was left in the cell, it will dilute our electrolytes slightly which can affect the results.

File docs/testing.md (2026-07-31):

---
Details:
    Time: Tens of minutes (preparation time), several days (experiment length)
    Skills:
      - General chemistry laboratory skills
---
<!-- There should be only one Header per page. You do not need to use all the keys -->

# Operating and testing the cell

{{BOM}}

## Weigh and add electrolyte to the cell{pagestep}

Using a [5 mL syringe]{qty: 1,cat: tool, Note: "or larger"} and the [scale]{qty: 1,cat: tool}, add 5 mL of [prepared electrolyte](fromstep) to each reservoir, weighing the syringe before and after injection to record the actual mass added to each reservoir. 

## Close the reservoirs{pagestep}

Carefully insert 19/22 silicone [septa][19/22 silicone septa](septa.md){qty: 2,cat: part} into the reservoirs and fold them over to seal them.




## Pre-circulate the electrolyte{pagestep}

Turn the pumps on and circulate the electrolytes for 15 min before applying any current. 

>i **Note** 
>i
>i This should allow enough time for the separator to become fully wetted with electrolyte and clear out any bubbles trapped in the cell/felts.

## Connect to the potentiostat and define cycling conditions{pagestep}

>!! **Warning** 
>!!
>!! Enclose the battery when cycling - you can put it inside a plastic tub - because leaks due to any problem will spray charged electrolyte, which, even if the volume is low, can be dangerous.

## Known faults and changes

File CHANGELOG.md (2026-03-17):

# Changelog

All notable changes to this project will be documented in this file.

The format is based on [Keep a Changelog](https://keepachangelog.com/en/1.1.0/),
and this project adheres to [Semantic Versioning](https://semver.org/spec/v2.0.0.html).

## Upcoming [1.X.0]

### Added

- Cable channels and power jack to Arduino case to tidy the wiring on the rear of the kit
- OSHWA certification
- Early-stage continuous integration into the repository with ForgeJo Actions, to allow for FreeCAD exports
- Specification of GN 1/3 150 mm depth plastic container to contain kit
- Arrows on reservoirs to indicate fluid flow

### Fixed

- STL exports should have correct orientation for 3D printing upon export from FreeCAD

### Changed

- Diameters of barb clearance holes changed from 8.5 to 10.5 mm, as outer current collector/endplate were too tight of a fit, and 10.5 mm will fit a Luer-Lok adapter through it.
- Sealing mechanism - cell now closed with C-clamp instead of bolts. This changed the endplate design. It is backwards-compatible with existing current collectors/graphite/gasket designs.
- Jig and reservoir design to fit in container
- Reservoirs now joined, with the option of having a spillover between them (enabled by default)

### Removed

- Removed two bolt holes from grafoil and gaskets as no longer needed with new sealing mechanism

## [1.0.0] 2025-07-25

### Added

- A jig to help assemble the cell

### Fixed

- Proper PTFE-lined tubing now specified for use with triiodide-containing electrolytes

### Changed

- Cell design. Barbs now are printed onto the flow frame, and extend out through a FDM-printable endplate. The endplate can be printed in a rigid, yet non-chemically-compatible material (like PLA/PETG), while the flow path can be fully polypropylene. All flow cell components have changed.
- Pumps are now peristaltic, not diaphragm. 
- Current collectors are brass now, not copper.
- Option of titanium fasteners for more resistance against trace triiodide when disassebling cell
- File structure of repo, location of FreeCAD, KiCAD files
- FreeCAD structure: there is now one `assembly.FCStd` file, holding all the other parts, with a `VarSet` that can control most of the changeable parameters

### Removed

## [0.0.2] 2025-01-05

### Added

- Brief documentation on cell operation, disassembly, data analysis
- Source for silicone septa

### Fixed

- Assembly order of pumps in jig

## [0.0.1] - 2024-12-30

### Added

- Everything, it's the first release!

### Fixed

### Changed

### Removed

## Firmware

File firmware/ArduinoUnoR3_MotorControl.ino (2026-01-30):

#include <elapsedMillis.h>
#define LED_BUILTIN 17

// YELLOW WIRES, SPEED MEASUREMENT
#define PIN_1P_TACHO 2
#define PIN_1N_TACHO 3

// GREEN WIRES, DIRECTION
#define PIN_1P_DIR 6
#define PIN_1N_DIR 7

// WHITE WIRES, SPEED CONTROL

#define PIN_1P_PWM 10
#define PIN_1N_PWM 11

// INPUT PUMP SPEED/DUTY CYCLE, 0-255 is 0-100%, PUMPS MINIMUM SPEED STARTS FROM ~3.8 - 7.6 %
int set1P = 0;
int set1N = 0;

// OUTPUT PUMP SPEED

unsigned long rpm1P = 0;
unsigned long rpm1N = 0;

//PUMP COUNTERS

unsigned long count1P = 0;
unsigned long count1N = 0;

const byte buffSize = 40;
char inputBuffer[buffSize];
const char startMarker = '<';
const char endMarker = '>';
byte bytesRecvd = 0;
boolean readInProgress = false;
boolean newDataFromPC = false;
char messageFromPC[buffSize] = {0};
char cmd;
String val;

const int updateInterval = 1000; // serial update time period (ms)
elapsedMillis updateTimer = 0;

bool ledState = LOW;



void parseData()
{
  cmd = strtok(inputBuffer, ",")[0];
  val = strtok(NULL, ",");
  //Serial.print(cmd);
  //Serial.print(',');
  //Serial.println(val);
}

void recieveFromPC()
{

  // receive data from PC and save it into inputBuffer

  if (Serial.available() > 0)
  {

    char x = Serial.read();
    // the order of these IF clauses is significant

    if (x == endMarker)
    {
      readInProgress = false;
      newDataFromPC = true;
      inputBuffer[bytesRecvd] = 0;
      parseData();
    }

    if (readInProgress)
    {
      inputBuffer[bytesRecvd] = x;
      bytesRecvd++;
      if (bytesRecvd == buffSize)
      {
        bytesRecvd = buffSize - 1;
      }
    }

    if (x == startMarker)
    {
      bytesRecvd = 0;
      readInProgress = true;
    }
  }
}

void ISR_1P()
{
  count1P++;
}
void ISR_1N()
{
  count1N++;
}

void setup()
{
  Serial.begin(9600);

  pinMode(LED_BUILTIN, OUTPUT);
  digitalWrite(LED_BUILTIN, ledState);

  pinMode(PIN_1P_PWM, OUTPUT);
  pinMode(PIN_1N_PWM, OUTPUT);
  pinMode(PIN_1P_DIR, OUTPUT);
  pinMode(PIN_1N_DIR, OUTPUT);


  digitalWrite(PIN_1P_DIR, LOW);
  digitalWrite(PIN_1N_DIR, HIGH);

  analogWrite(PIN_1P_PWM, set1P);
  analogWrite(PIN_1N_PWM, set1N);

  pinMode(PIN_1P_TACHO, INPUT_PULLUP);
  pinMode(PIN_1N_TACHO, INPUT_PULLUP);
  attachInterrupt(digitalPinToInterrupt(PIN_1P_TACHO), ISR_1P, RISING);
  attachInterrupt(digitalPinToInterrupt(PIN_1N_TACHO), ISR_1N, RISING);
}

void controlPumps()
{
  if (newDataFromPC)
  {
    switch (cmd)
    {
    case 'a':
      set1P = val.toInt();
      analogWrite(PIN_1P_PWM, set1P);
      break;
    case 'b':
      set1N = val.toInt();
      analogWrite(PIN_1N_PWM, set1N);
      break;
    case 'c':
      set1N = val.toInt();
      set1P = val.toInt();
      analogWrite(PIN_1N_PWM, set1N);
      analogWrite(PIN_1P_PWM, set1P);
      break;
    }
  }
}

void replyToPC()
{
  if (updateTimer >= updateInterval)
  {

    noInterrupts();
    rpm1P = count1P * 60;
    rpm1N = count1N * 60;
    updateTimer = 0;
    count1P = 0;
    count1N = 0;
    interrupts();

    Serial.print(rpm1P);
    Serial.print(',');
    Serial.println(rpm1N);

  }
}

void loop()
{
  recieveFromPC();
  controlPumps();
  replyToPC();
}

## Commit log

2023-10-05 first attempt
    [alignment_pin.FCStd, assembly.FCStd, cell_body.FCStd, compressed_carbon_felt.FCStd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]
2023-10-18 1st version with 50x50mm plate, changelog, README
    [assembly.FCStd, assembly_1cm2.FCStd, bom.csv, cell_body.3mf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]
2023-10-18 updated 1cm2 FreeCAD assembly file
    [assembly_1cm2.FCStd]
2023-11-30 Design iterations
    [cell_body-Cell Body.3mf, cell_body.3mf, cell_body.FCStd, cell_body_4mm.FCStd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]
2023-12-09 Consolidated CAD to one file, added spreadsheet
    [alignment_pin.FCStd, assembly_1cm2.FCStd, cell_body-Cell Body.3mf, cell_body.FCStd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]
2023-12-09 changed Flow Field --> Flow Frame
    [flow_cell-Flow Frame.3mf, flow_cell.FCStd]
2023-12-11 added cura profile for polypropylene 0.8mm nozzle
    [flow_cell-Cell Body.3mf, flow_cell-Flow Frame.3mf, flow_cell.FCStd]
2024-01-02 sorting out git permissions
    [flow_cell.FCStd]
2024-01-02 adding git lfs
    [flow_cell-Cell Body.3mf, flow_cell-Flow Frame.3mf, flow_cell.FCStd, hole_tester.FCStd]
2024-01-02 removed hole tester
    [hole_tester.FCStd]
2024-01-02 trying feature-branch to add barbed fittings
    [flow_cell.FCStd]
2024-01-02 workflow established, incomplete
    [flow_cell.FCStd, flow_cell_barbed.3mf]
2024-01-02 updated barbed file
    [flow_cell_barbed.3mf]
2024-01-03 parametric barbed fittings, cloned base feature
    [Cell Body with Barbed Fittings.3mf, Cell Body with Flat-Bottom Ports.3mf, Flow Frame.3mf, flow_cell-Cell Body.3mf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]
2024-01-04 added STLs to render in gitbuilding docs
    [Cell Body with Barbed Fittings.stl, Flow Frame.stl]
2024-01-25 barbed fittings only fo r now, updated docs
    [Alignment Pins.stl, Backing Plate.3mf, Backing Plate.stl, Cell Body with Barbed Fittings.3mf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]
2024-01-25 update readme with docs link, delete bom
    [bom.csv]
2024-01-26 update docs with power electronics basics
    [Alignment Pins.stl, Backing Plate.stl, Cell Body with Four Barbed Fittings.stl, Flow Frame.stl]
2024-01-28 made cell thicc
    [Backing Plate.3mf, Backing Plate.stl, Cell Body with Four Barbed Fittings.3mf, Cell Body with Four Barbed Fittings.stl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]
2024-01-30 docs, added reservoir, made CAD folder
    [Barbed Fitting.3mf, Barbed Fitting.stl, Cell Body withOUT Two Barbed Fittings.3mf, Cell Body withOUT Two Barbed Fittings.stl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]
2024-01-31 made draft reservoir, jig in CAD folder
    [Incorrect Diaphragm Pump.STEP, L298N Motor Driver.STEP, Reservoir.3mf, Reservoir.stl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]
2024-02-01 meeting commit
    [Cell Body with Two Barbed Fittings.3mf, Cell Body with Two Barbed Fittings.stl, flow_cell.FCStd, jig.FCStd]
2024-02-01 moved exports to CAD dir, exports two-port cell
    [Alignment Pins.stl, Backing Plate.3mf, Backing Plate.stl, Barbed Fitting.3mf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]
2024-02-19 .step file for flow cell, updated reservoirs
    [Cell Body with Flat-Bottom Ports.step, Cell Body with Fluid Holes (no alignment holes).stl, Cell Body with Two Barbed Fittings (no alignment holes).3mf, Cell B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]
2024-03-03 first attempt at jig, reservoirs with septum
    [Alignment Pins.stl, Backing Plate.3mf, Backing Plate.stl, Barbed Fitting.stl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]
2024-03-05 next iteration of jig
    [Cell Body with Two Flat-Bottom Ports.stl, Flow Frame.stl, Reservoir.stl, flow_cell.FCStd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]
2024-03-05 updated jig and two port flat-bottom cell drawing
    [flow_cell.FCStd, jig.3mf, jig.FCStd, jig.stl]
2024-03-06 updated drawing to include material as PP/UMHW
    [flow_cell.FCStd, short_jig.3mf]
2024-03-17 new cover image render and some docs, jig updates
    [flow_cell.FCStd, jig.FCStd]
2024-03-18 playing with jig and renders
    [jig.FCStd, pump.FCStd]
2024-04-07 added 2 and 5.25 cm2 gaskets and flow frames
    [1 sqcm Flow Frame (Blocking).3mf, 1 sqcm Flow Frame (Pass-Through).3mf, 2 sqcm Flow Frame (Blocking).3mf, 5.25 sqcm Flow Frame (Blocking).3mf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]
2024-04-27 slight changes to docs
    [Cell Body with Two Barbed Fittings.stl, flow_cell.FCStd, membranes.dxf]
2024-04-27 made reservoirs beefier
    [Reservoir.3mf, reservoir.FCStd]
2024-04-27 updated reservoir stl export
    [reservoir-Reservoir.stl]
2024-04-28 updated membrane shape for better sealing
    [flow_cell.FCStd, membranes.dxf]
2024-05-01 updated reservoir.stl
    [Reservoir.stl, reservoir-Reservoir.stl]
2024-05-19 updated jig for peristaltic pumps, added +/- labels and FBRC label to jig
    [Barbed Fitting.3mf, barb.FCStd, flow_cell.FCStd, jig.3mf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]
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2024-07-03 some steps on power electronics added to gitbuilding docs
    [flow_cell.FCStd]
2024-08-14 added membrane frame for spacing of thick membranes
    [Membrane Frame (For Thick Membranes).3mf, Membrane Frame (For Thick Membranes).stl, flow_cell.FCStd]
2024-08-15 added warning of incomplete docs, membrane spacer
    [flow_cell.FCStd]
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2024-09-10 Flow frames of various thicknesses and area from current flow cell FreeCAD file
    [1 sqcm 0.6 mm Flow Frame.stl, 1 sqcm 0.8 mm Flow Frame.stl, 2 sqcm 0.6 mm Flow Frame.stl, 2 sqcm 0.8 mm Flow Frame.stl]
2024-09-10 Rest of flow frames from previous commit
    [1 sqcm 1.0 mm Flow Frame.stl, 1 sqcm 1.2 mm Flow Frame.stl, 2 sqcm 1.0 mm Flow Frame.stl, 2 sqcm 1.2 mm Flow Frame.stl]
2024-10-04 updated cad files for FreeCAD 1.0.0RC2, changed grafoil geometry for better seal, default 2 cm2 cell
    [flow_cell.FCStd, jig.FCStd, reservoir.FCStd]
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2024-11-17 new feature branch for square cell with barbed flow frames and non-chemically-compatible compression plate
    [flow_cell.FCStd]
2024-11-18 first draft of fully-printable cell, most components in
    [flow_cell.FCStd]
2024-11-20 added tabs to Cu plate, FreeCAD 1.0
    [flow_cell.FCStd]
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2024-11-22 CAD work - simplified polymer endplate, removed old export files, generated some new export files
    [1 sqcm 0.6 mm Flow Frame.stl, 1 sqcm 0.8 mm Flow Frame.stl, 1 sqcm 1.0 mm Flow Frame.stl, 1 sqcm 1.2 mm Flow Frame.stl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]
2024-11-22 updated CAD exports
    [Metal Endplate.step, Polymer Endplate.stl, flow_cell.FCStd]
2024-11-27 updated docs a bit, messed with CfdOF and flow field
    [Membrane Frame (For Thick Membranes).stl, Membrane Frame.stl, Reservoir.stl, flow_cell.FCStd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]
2024-12-27 made jig for assembling barbed cell more easily with attached tubing
    [Cell Assembly Jig.stl, Endplate.stl, Polymer Endplate.stl, cell-assembly-jig.FCStd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]
2025-01-18 changing file structure to match LumenPNP - one mechanical part, one FreeCAD file
    [2 sqcm 0.5 mm wall Flow Frame.stl, 2 sqcm 0.6 mm wall Flow Frame.stl, 2 sqcm 0.7 mm wall Flow Frame.stl, 2 sqcm 2.0 mm Flow Frame.stl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]
2025-01-19 finished CAD file restructure, flow cell and jig assembly now in assembly.FCStd, flow frame barb fillet incresed 1->2 mm
    [CFD.FCStd, assembly.FCStd, flow-frame.FCStd, inner-current-collector.FCStd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]
2025-01-23 updating docs for barbed cell
    [Cell Assembly Tool.stl, cell-assembly-tool.FCStd]
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2025-02-28 Fixed double reservoir so septas can properly close, current collector brass, added back reservoir.FCStd
    [Double Reservoir.stl, double-reservoir.FCStd]
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2025-03-29 CAD and docs: redesign jig to add separate Arduino case, remove back of jig, adjust docs to match
    [assembly.FCStd, jig.FCStd, jig.stl, reset_button.stl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]
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2025-04-15 positive pump hole now correct size
    [assembly.FCStd, jig.FCStd, jig.stl]
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2025-05-12 CAD: got rid of motor driver file, fixed assembly file
    [L298N Motor Driver.STEP, assembly.FCStd]
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2026-02-02 CAD: change barb clearance hole in endplate and brass plate to 9.5 mm
    [outer-current-collector.FCStd, polymer-endplate.FCStd]
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2026-02-10 CAD: barb clearance hole 9.5 -> 10.5 mm
    [Endplate (Hole).stl, Endplate (Pin).stl]
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2026-03-04 CAD: add indents on endplates to allow for clamp centering, add another clip for reservoir to fix vertical height, fixed reservoirs which had a blocked fluid passage after last redesign, rotate cell 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
    [Double Reservoir.stl, Endplate (Hole).stl, Endplate (Pin).stl, assembly.FCStd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]
2026-03-04 CAD: cleaned up exports folder, updated everything for 10.5 mm diameter barb clearance holes to allow for Luer-Lok fittings to pass, updated current collector, grafoil, gaskets to reflect this and re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
    [Current Collector.step, Jig.stl, Metal Endplate.step, Polymer Endplate.stl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]
2026-03-17 added export script, minor docs edits, fix endplate barb hole diameters (again?), STLs should export with correct orientation now
    [2 sqcm 0.7 mm wall Flow Frame.stl, Cell Assembly Tool.stl, Cell-Assembly-Tool.stl, Current-Collector.step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]
2026-03-18 improving CI/CD for PDF/SVG export from TechDraw, fix threads issues
    [Current-Collector.step, assembly.FCStd, outer-current-collector.FCStd]
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2026-03-27 CAD: rotate current collector 90 deg to give more clearance in GN 1/3 container while allowing for vertical, gas-clearing flow. Also update to FreeCAD 1.1 stable. Change video link in docs
    [Clamp.FCStd, Current-Collector.step, GN_Container.FCStd, assembly.FCStd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]
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2026-04-20 trying to fix the dag problem in assembly file
    [assembly.FCStd, luer-tool-1_4_ Drive.stl, luer-tool-Angled Open-Ended Spanner.stl, luer-tool-Open-Ended Spanner.stl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]
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
